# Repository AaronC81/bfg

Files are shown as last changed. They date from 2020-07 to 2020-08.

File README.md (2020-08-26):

# The BFG - Basic Function Generator

The BFG is a small, minimalistic function generator based around the
[AD9833](https://www.analog.com/media/en/technical-documentation/data-sheets/AD9833.pdf),
controlled by an ATmega328P with a lovely little OLED display and rotary
encoder.

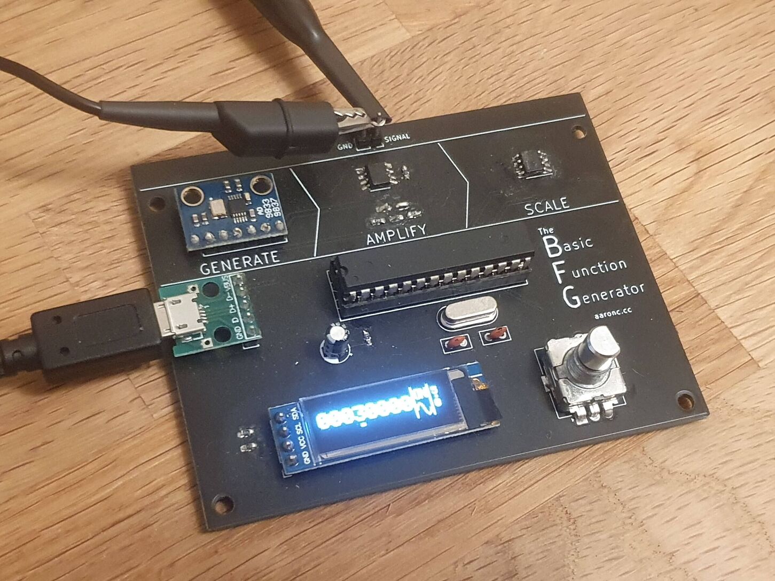
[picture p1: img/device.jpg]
An assembled BFG, with an OLED display, rotary encoder, three generation ICs, and an ATmega328P microcontroller.


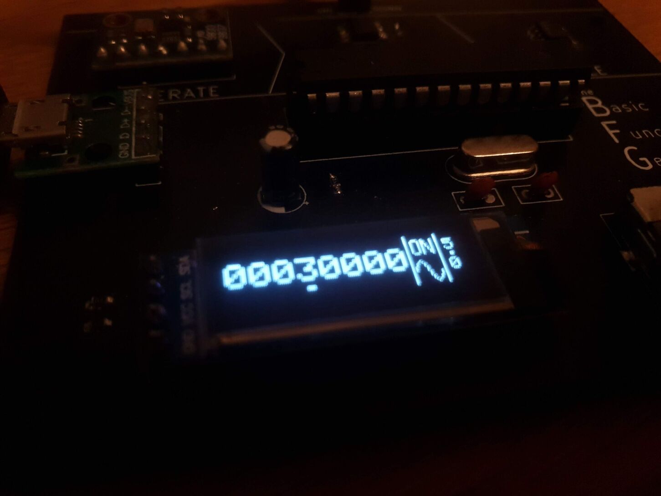
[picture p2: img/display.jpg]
The BFG's display, showing frequency, wave type, power switch, and amplitude.


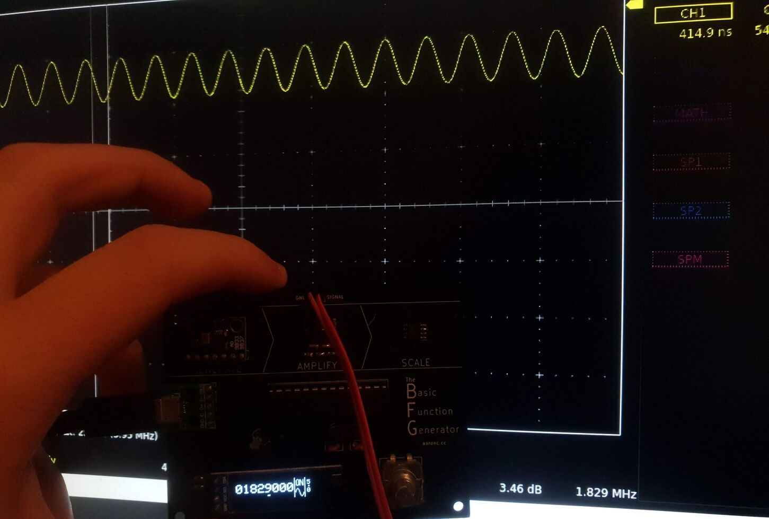
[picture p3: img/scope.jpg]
The oscilloscope output from the BFG, with the BFG and scope showing the same frequency to 3dp.


- Sine, square and triangle waves
- Powered over Micro USB
- Output range of 0 to 5 volts
- Theoretical maximum output frequency of 12.5MHz

At high frequencies (>2MHz) the range of voltages begins to narrow; for example,
a sine wave at 5MHz set to an amplitude of 5V only actually oscillates between
about 1.5V and 4V. These frequencies are a tad much for my poor USB oscilloscope
to handle, so I can't accurately measure the practical limits.

I built this for two main reasons:

- To have a basic function generator for embedded projects
- To learn simple surface-mount soldering

# How it Works

As the rather lovely silkscreen on the board suggests, functions are generated
by three steps:

1. **Generate**: The AD9833 generates a low-voltage signal, about 0.65V
2. **Amplify**: The AD8052 op-amp amplifies the signal to 5V
3. **Scale**: The MCP4131 digital potentiometer divides the signal down to the desired amplitude

# Repo

`cad` contains KiCad files for the PCB.

`firmware` contains a platform.io project for the ATmega328P's firmware.

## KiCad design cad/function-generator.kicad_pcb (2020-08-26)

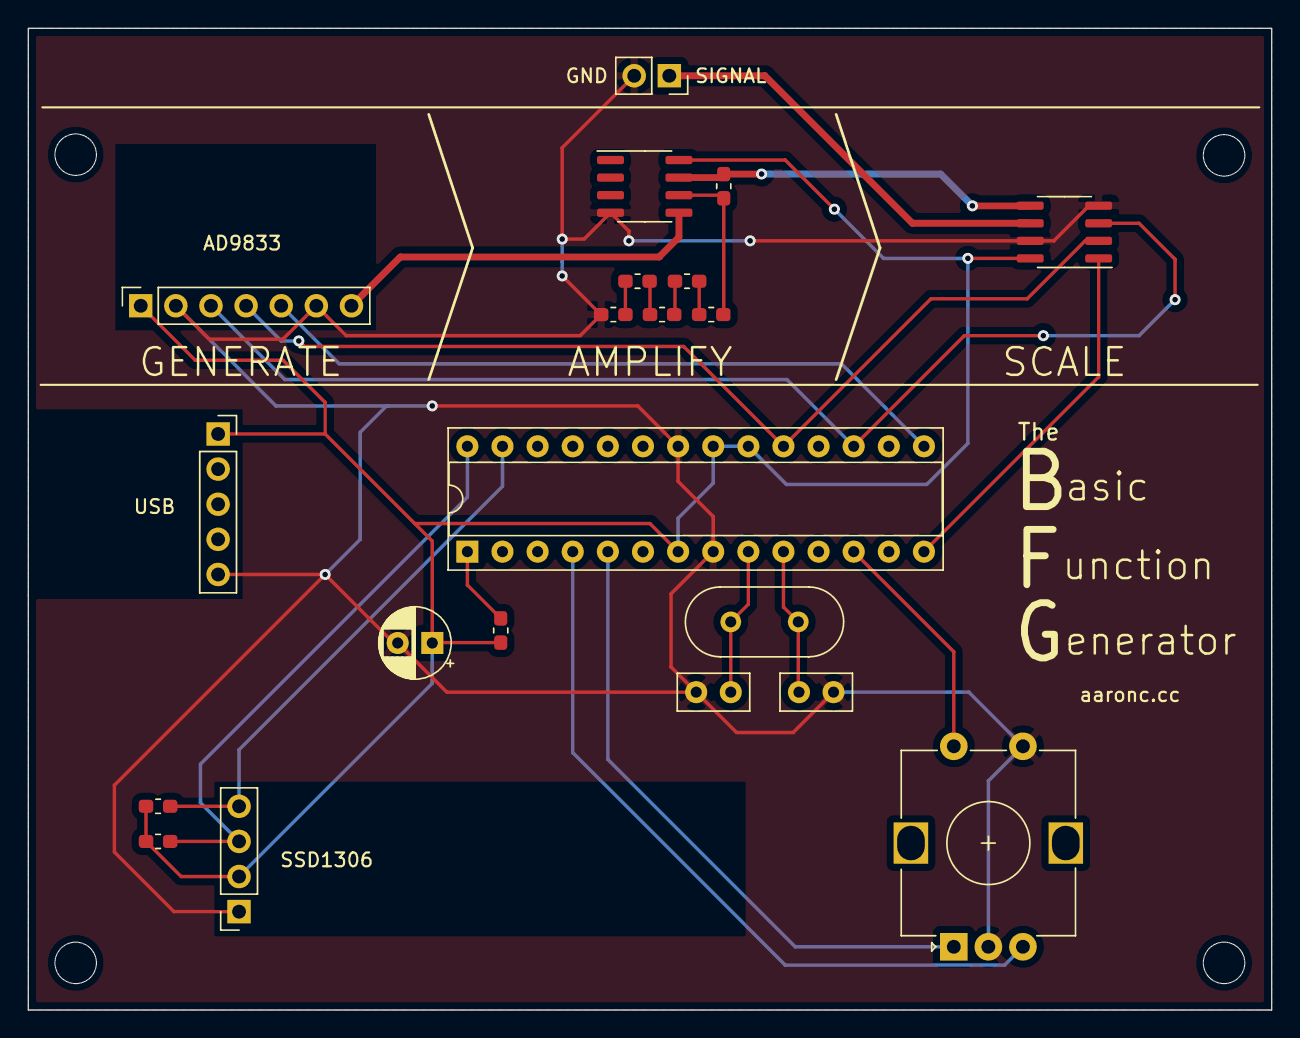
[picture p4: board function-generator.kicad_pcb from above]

Board: 2 copper layers, 89.9 x 71.0 mm, 21 parts (0 on the bottom side), 22 nets.

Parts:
C1: 10uF; CP_Radial_D5.0mm_P2.50mm
C2, C3: 22pF; C_Disc_D5.0mm_W2.5mm_P2.50mm
J1: USB_B_Micro_NoShield; PinSocket_1x05_P2.54mm_Vertical
J2: Conn_01x02_Female; PinSocket_1x02_P2.54mm_Vertical
R1, R2, R3, R12: 4.7k; R_0603_1608Metric_Pad1.05x0.95mm_HandSolder
R7: 680; R_0603_1608Metric_Pad1.05x0.95mm_HandSolder
R8: 10; R_0603_1608Metric_Pad1.05x0.95mm_HandSolder
R9, R10, R11: 4.7; R_0603_1608Metric_Pad1.05x0.95mm_HandSolder
SW1: Rotary_Encoder_Switch; RotaryEncoder_Alps_EC12E-Switch_Vertical_H20mm
U1: ATmega328P-PU; DIP-28_W7.62mm_Socket
U2: SSD1306_128x32; PinSocket_1x04_P2.54mm_Vertical
U3: MCP4131; SOIC-8_3.9x4.9mm_P1.27mm
U4: AD9833_Breakout; PinSocket_1x07_P2.54mm_Vertical
U5: AD8052; SOIC-8_3.9x4.9mm_P1.27mm
Y1: 16MHz; Crystal_HC49-4H_Vertical

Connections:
5VSIG: R12.1, U3.5, U5.7
FGCS: U1.15, U4.5
GND: C1.2, C2.2, C3.2, J1.5, J2.2, R11.2, SW1.C, SW1.S2, U1.8, U1.22, U2.1, U3.4, U3.7, U4.2, U4.6, U5.4
MOSI: U1.17, U3.3, U4.3
unnamed: R3.2, U1.1
unnamed: R7.2, R8.1
unnamed: R8.2, R9.1
unnamed: R9.2, R10.1
unnamed: R10.2, R11.1
unnamed: R7.1, R12.2, U5.6
POTCS: U1.14, U3.1
ROTCLK: SW1.A, U1.5
ROTDT: SW1.B, U1.4
ROTSW: SW1.S1, U1.12
SCK: U1.19, U3.2, U4.4
SCL: R2.2, U1.28, U2.3
SDA: R1.2, U1.27, U2.4
SIG: J2.1, U3.6
VCC: C1.1, J1.1, R1.1, R2.1, R3.1, U1.7, U1.20, U1.21, U2.2, U3.8, U4.1, U5.8
WEAKSIG: U4.7, U5.5
XTAL1: C2.1, U1.9, Y1.1
XTAL2: C3.1, U1.10, Y1.2

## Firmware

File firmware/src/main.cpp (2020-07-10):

#include <SPI.h>
#include <Wire.h>
#include <Adafruit_GFX.h>
#include <Adafruit_SSD1306.h>
#include <MD_AD9833.h>
#include <Encoder.h>

#define ROTARY_ENCODER_DT 2
#define ROTARY_ENCODER_CLK 3
#define ROTARY_ENCODER_SW 6
Encoder encoder(ROTARY_ENCODER_CLK, ROTARY_ENCODER_DT);

#define DDS_FSYNC 9
#define DDS_SCLK 13
#define DDS_SDATA 11
MD_AD9833 dds(DDS_FSYNC);

#define POT_CS 8

#define DISPLAY_WIDTH 128
#define DISPLAY_HEIGHT 32

#define ICON_SIZE 14

Adafruit_SSD1306 display = Adafruit_SSD1306(DISPLAY_WIDTH, DISPLAY_HEIGHT, &Wire);

struct func_menu_item {
  char *title;
  uint8_t *icon;
  MD_AD9833::mode_t dds_mode;
};

uint8_t sine_wave_icon[] = {
  0xef, 0xfc, 0xd7, 0xfc, 0xbb, 0xfc, 0xbb, 0xfc, 0x7d, 0xfc, 0x7d, 0xfc, 0x7d, 0xfc, 0xfe, 0xf8, 
  0xfe, 0xf8, 0xfe, 0xf8, 0xff, 0x74, 0xff, 0x74, 0xff, 0xac, 0xff, 0xdc
};

uint8_t square_wave_icon[] = {
  0x00, 0xfc, 0xfe, 0xfc, 0xfe, 0xfc, 0xfe, 0xfc, 0xfe, 0xfc, 0xfe, 0xfc, 0xfe, 0xfc, 0xfe, 0xfc, 
  0xfe, 0xfc, 0xfe, 0xfc, 0xfe, 0xfc, 0xfe, 0xfc, 0xfe, 0xfc, 0xfe, 0x00
};

uint8_t triangle_wave_icon[] = {
  0xef, 0xfc, 0xd7, 0xfc, 0xd7, 0xfc, 0xbb, 0xfc, 0xbb, 0xfc, 0x7d, 0xfc, 0x7d, 0xfc, 0xfe, 0xf8, 
  0xfe, 0xf8, 0xff, 0x74, 0xff, 0x74, 0xff, 0xac, 0xff, 0xac, 0xff, 0xdc
};

uint8_t on_icon[] = {
  0xff, 0xfc, 0xff, 0xfc, 0xc6, 0xf4, 0xba, 0x74, 0xba, 0x74, 0xba, 0xb4, 0xba, 0xb4, 0xba, 0xd4, 
  0xba, 0xd4, 0xba, 0xe4, 0xba, 0xe4, 0xc6, 0xf4, 0xff, 0xfc, 0xff, 0xfc
};

uint8_t off_icon[] = {
  0xff, 0xfc, 0xff, 0xfc, 0xcc, 0x44, 0xb5, 0xdc, 0xb5, 0xdc, 0xb5, 0xdc, 0xb4, 0x44, 0xb5, 0xdc, 
  0xb5, 0xdc, 0xb5, 0xdc, 0xb5, 0xdc, 0xcd, 0xdc, 0xff, 0xfc, 0xff, 0xfc
};

#define INVERT_BITMAP(x) for (int i = 0; i < sizeof(x); i++) x[i] = ~x[i];

// http://javl.github.io/image2cpp/ outputs with the wrong colours, and it won't change for some reason.
// This inverts the colour. 
void prepare_bitmaps() {
  INVERT_BITMAP(sine_wave_icon);
  INVERT_BITMAP(square_wave_icon);
  INVERT_BITMAP(triangle_wave_icon);
  INVERT_BITMAP(on_icon);
  INVERT_BITMAP(off_icon);
}

// The array of available functions.
struct func_menu_item funcs[] = {
  { .title = "Sine", .icon = sine_wave_icon, .dds_mode = MD_AD9833::mode_t::MODE_SINE },
  { .title = "Square", .icon = square_wave_icon, .dds_mode = MD_AD9833::mode_t::MODE_SQUARE1 },
  { .title = "Triangle", .icon = triangle_wave_icon, .dds_mode = MD_AD9833::mode_t::MODE_TRIANGLE },
};

// Whether the function generator is currently enabled.
bool enabled = true;

// The number of functions.
uint16_t funcs_len = 3;

// The current function index.
uint16_t func = 0;

// The current frequency.
uint32_t freq = 10000;

// The whole part of the current amplitude.
uint8_t amplitude_whole = 5;

// The decimal part of the current amplitude.
uint8_t amplitude_decimal = 0;

// The currently selected digit. 0 indexed, and there are 8 digits.
// A value of > 7 indicates a special function.
uint8_t ui_current_item = 0;
#define UI_FIRST_SPECIAL_ITEM 8
#define UI_CURRENT_ITEM_ENABLED 8
#define UI_CURRENT_ITEM_FUNCTION 9
#define UI_CURRENT_ITEM_AMPLITUDE 10
#define UI_LAST_ITEM 10

// Whether the selected digit is being actively edited.
bool ui_editing = false;

void freq_draw() {
  display.clearDisplay();

  // Write digits
  // TODO: would be neat to group digits
  const int character_width = 12;
  const int total_text_width = 8 * character_width;
  const int text_pad = 0;
  const int icon_pad = 1;
  display.setTextSize(2);
  display.setTextColor(1);
  display.setCursor(text_pad, 8);
  char frequency[9];
  sprintf(frequency, "%08lu", freq);
  display.print(frequency);

  // Draw separator line after frequency
  display.drawLine(total_text_width + text_pad * 2, 0, total_text_width + text_pad * 2, DISPLAY_HEIGHT, 1);

  // Draw enabled icon
  int enabled_icon_colour = 1;
  if (ui_current_item == UI_CURRENT_ITEM_ENABLED) {
    display.fillRect(total_text_width + text_pad * 2, 0, icon_pad * 2 + ICON_SIZE, DISPLAY_HEIGHT / 2, 1);
    enabled_icon_colour = 0;
  }
  display.drawBitmap(total_text_width + text_pad * 2 + 2, 1, enabled ? on_icon : off_icon, ICON_SIZE, ICON_SIZE, enabled_icon_colour);

  // Draw signal icon
  int signal_icon_colour = 1;
  if (ui_current_item == UI_CURRENT_ITEM_FUNCTION) {
    display.fillRect(total_text_width + text_pad * 2, DISPLAY_HEIGHT / 2, icon_pad * 2 + ICON_SIZE, DISPLAY_HEIGHT / 2, 1);
    signal_icon_colour = 0;
  }
  display.drawBitmap(total_text_width + text_pad * 2 + 2, (DISPLAY_HEIGHT / 2) + 1, funcs[func].icon, ICON_SIZE, ICON_SIZE, signal_icon_colour);

  const int amplitude_start = total_text_width + text_pad * 2 + icon_pad * 2 + ICON_SIZE + 1;

  // Draw separator line after enabled/signal
  display.drawLine(amplitude_start, 0, amplitude_start, DISPLAY_HEIGHT, 1);

  // Draw amplitude
  display.setTextSize(1);
  display.setCursor(amplitude_start + 4, 4);
  display.write('0' + amplitude_whole);
  display.setCursor(amplitude_start + 4, 8);
  display.print(".");
  display.setCursor(amplitude_start + 4, 17);
  display.write('0' + amplitude_decimal);
  if (ui_current_item == UI_CURRENT_ITEM_AMPLITUDE) {
    if (ui_editing) {
      display.fillRect(amplitude_start + 2, 26, 10, 2, 1);
    } else {
      display.fillRect(amplitude_start + 4 + 1, 26, 4, 2, 1);
    }
  }

  // Draw current digit underline/selection
  if (ui_current_item < UI_FIRST_SPECIAL_ITEM) {
    int selection_x = ui_current_item * character_width + text_pad;
    if (ui_editing) {
      display.fillRect(selection_x, 26, character_width, 2, 1);
    } else {
      display.fillRect(selection_x + character_width / 3, 26, character_width / 3, 2, 1);
    }
  }

  display.display();
}

void amplitude_inc() {
  // Hard limit of 5V

  if (amplitude_whole == 5) return;

  if (amplitude_decimal == 9) {
    amplitude_decimal = 0;
    amplitude_whole++;
  } else {
    amplitude_decimal++;
  }
}

void amplitude_dec() {
  if (amplitude_whole == 0 && amplitude_decimal == 0) return;

  if (amplitude_decimal == 0) {
    amplitude_decimal = 9;
    amplitude_whole--;
  } else {
    amplitude_decimal--;
  }
}

void freq_inc_selected() {
  uint32_t base = 1;
  for (int i = 0; i < UI_FIRST_SPECIAL_ITEM - ui_current_item; i++)
    base *= 10;
  int digit = (freq / (base / 10)) % 10;
  if (digit == 9) {
    freq -= (base / 10) * 9;
  } else {
    freq += base / 10;
  }
}

void freq_dec_selected() {
  uint32_t base = 1;
  for (int i = 0; i < UI_FIRST_SPECIAL_ITEM - ui_current_item; i++)
    base *= 10;
  int digit = (freq / (base / 10)) % 10;
  if (digit == 0) {
    freq += (base / 10) * 9;
  } else {
    freq -= base / 10;
  }
}

enum input {
  INPUT_NONE = 0,
  INPUT_LEFT,
  INPUT_RIGHT,
  INPUT_SELECT,
};

long last_rotary_encoder_state = -999;

enum input input_get() {
  enum input result = INPUT_NONE;
  long curr_rotary_encoder_state = encoder.read() / 4;

  if (!digitalRead(ROTARY_ENCODER_SW)) {
    return INPUT_SELECT;
  }

  if (curr_rotary_encoder_state > last_rotary_encoder_state) {
    result = INPUT_LEFT;
  } else if (curr_rotary_encoder_state < last_rotary_encoder_state) {
    result = INPUT_RIGHT;
  }

  last_rotary_encoder_state = curr_rotary_encoder_state;

  return result;
}

void dds_update() {
  dds.setFrequency(MD_AD9833::CHAN_0, freq);
  dds.setMode(enabled ? funcs[func].dds_mode : MD_AD9833::mode_t::MODE_OFF);
}

void pot_set(int value) {
  digitalWrite(POT_CS, LOW);
  SPI.transfer(0);
  SPI.transfer(value);
  digitalWrite(POT_CS, HIGH);
}

void pot_update() {
  int pot_value = ((float)(amplitude_whole * 10 + amplitude_decimal) / 50) * 128;
  pot_set(pot_value);
}

void setup() {
  Serial.begin(9600);
  pinMode(ROTARY_ENCODER_DT, INPUT_PULLUP);
  pinMode(ROTARY_ENCODER_CLK, INPUT_PULLUP);
  pinMode(ROTARY_ENCODER_SW, INPUT_PULLUP);
  pinMode(DDS_FSYNC, OUTPUT);
  pinMode(DDS_SCLK, OUTPUT);
  pinMode(DDS_SDATA, OUTPUT);
  pinMode(POT_CS, OUTPUT);
  digitalWrite(DDS_FSYNC, HIGH);
  digitalWrite(POT_CS, HIGH);

  prepare_bitmaps();

  display.begin(SSD1306_SWITCHCAPVCC, 0x3C); // Address 0x3C for 128x32
  display.display();

  SPI.begin();
  dds.begin();
  dds_update();
  pot_update();
  
  display.clearDisplay();
  freq_draw();
}

void loop() {
  switch (input_get()) {
  case INPUT_LEFT:
    if (ui_editing) {
      if (ui_current_item == UI_CURRENT_ITEM_AMPLITUDE) {
        amplitude_dec();
        pot_update();
      } else {
        freq_dec_selected();
        dds_update();
      }
    } else if (ui_current_item == 0) {
      ui_current_item = UI_LAST_ITEM;
    } else {
      ui_current_item--;
    }
    dds_update();
    freq_draw();
    break;
  case INPUT_RIGHT:
    if (ui_editing) {
      if (ui_current_item == UI_CURRENT_ITEM_AMPLITUDE) {
        amplitude_inc();
        pot_update();
      } else {
        freq_inc_selected();
        dds_update();
      }
    } else if (ui_current_item == UI_LAST_ITEM) {
      ui_current_item = 0;
    } else {
      ui_current_item++;
    }
    freq_draw();
    break;
  case INPUT_SELECT:
    if (ui_current_item == UI_CURRENT_ITEM_ENABLED) {
      enabled = !enabled;
      dds_update();
    } else if (ui_current_item == UI_CURRENT_ITEM_FUNCTION) {
      if (func == funcs_len - 1) {
        func = 0;
      } else {
        func++;
      }
      dds_update();
    } else {
      ui_editing = !ui_editing;
    }
    freq_draw();
    delay(200);
    break;
  default:
    break;
  }
  delay(1);
}
